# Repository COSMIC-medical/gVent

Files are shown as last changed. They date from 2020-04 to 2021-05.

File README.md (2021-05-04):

# The Gravity Ventilator (gVent)

Video introduction to the design [here](https://www.youtube.com/watch?v=yVxmjUQLIBw)
### A COSMIC Medical Project

This repository contains all the design files necessary to assemble a gravity ventilator. Please read license.pdf before using any of the files to understand the liabilities and limitations you are responsible for by using this repository.

NOTE: At this point, this is not a medical device, meaning that the device is NOT medically approved for human use, and as such, improper use can result in harm or death of anyone using the ventilator. It is still in its development stages and any use in a clinical setting should be under the strict consultation and supervision of qualified healthcare experts and/or qualified biomedical engineers.

## Background on the Idea

In February 2020 amidst the CoVid-19 pandemic, concerns about a global shortage of ventilators began to surface and these discussions rapidly became a reality. We sought out to find a local solution to the rapidly evolving crisis, working alongside the [hundreds of open-source projects worldwide](https://github.com/PubInv/covid19-vent-list), aimed at tackling the same problem.

We believe that we add a novel solution to a landscape dominated by automated bag-valve mask compression devices. Built using readily-available materials and utilizing resources routinely found at a patient’s bedside, our aims were to produce a device capable of being produced at a sub-$100 price point for low-resource settings, as well as a more robust model, both founded using the same principles.
## The Design

Modern commercial ventilators are complex machines with specialized components. According to the Department of Health and Social Care guidance statement on [Rapidly Manufactured Ventilator System Specification (20/03/2020)](), ventilators must meet certain criteria to be considered “clinically acceptable”.

RMVS-compatible ventilators must be capable of providing one of two modes of ventilation. The first is mandatory ventilation, wherein the patient is completely sedated, and all work of breathing must be done by the ventilator, according to preset criteria (e.g. tidal volume, respiratory rate, E/I ratio). Supportive ventilation, on the other hand, is used when the patient can do some work on their own. The machine must be able to sense when the patient is attempting to inhale (and provide inspiratory support), and when the patient is exhaling (and provide expiratory support).

#### __How does it work?__

The basis of the gVent system is gravity, water, and two cylindrical vessels fitted together to create a pressurized system. This pressure can then be used to ventilate a sick patient. The two vessels are each sealed at one end. The larger vessel is filled with water; the smaller vessel is placed inside the larger vessel.

Air is then introduced into the system from the hospital's O<sub>2</sub> outlet. A clinician can thus control the FiO<sub>2</sub> by titrating the amount of hospital air to the amount of delivered O<sub>2</sub>. As this pressurized gas builds up in the system, the top cylinder is displaced upwards from its resting position, commensurate to the weight of the top cylinder (which can have weight added to adjust the pressure).

To deliver air, a valve is opened, releasing the pressurized air/O<sub>2</sub> mixture through to the intubated patient. And with the valve controlled on an electronic circuit, the operator has the ability to control important respiratory parameters, including respiratory rate, I:E ratio, and the volume of air delivered to the patient.

## Bill of Materials

## Installation Instructions

1. The Assembly Instructions document for the gVent can be found at [The COSMIC Medical Website](https://cosmicmedical.ca/gvent-722-warnings-disclaimers).
2. In order to view the code and upload it to the Arduino, download and install the [Arduino IDE](https://www.arduino.cc/en/Main/Software).

## Contributing
See the [CONTRIBUTOR.md](./CONTIBUTOR.md) file in the root of the repository for guidelines and additional instructions.

## Licensing Notes
As per our understanding, hardware is not covered by copyright. However, we present our work under the TAPR OHL license insofar as it applies. All software and documentation is licensed under Apache 2.0.

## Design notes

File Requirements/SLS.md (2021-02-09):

# Gravity Ventilator (gVent) – System Level Specification

***

| Document ID | CSL0133 |
| :-- | :-- |
| Status | DRAFT | 
| Prepared For | COSMIC |
| Project Name | gVent |
| Publish Date | 2020-09-28 |
| Version | 0.8 |

***

# Table of Contents
ii. Document History
1.	[Introduction](#introduction)	
- 1.1	Purpose and scope
- 1.2	Document Structure
- 1.3	Referenced Documents	
2.	System Identification	
- 2.1	System Overview	
- 2.2	Regulatory Environment	
3.	[General](#General)
4.	[Ventilation](#Ventilation)
5.	[Performance](#Performance)
6.	[Alarm](#Alarm)
7.	Major Failure Response
8.	[Reliability](#Reliability)	
9.	[Glossary](#Glossary)

# Document History
| Version | Date | Revision Summary |
| :-- | :-- | :-- |
| 0.1 | 2020-09-24 | First draft |
| 0.2 | 2020-09-25 | Addition of Background information |
| 0.3 | 2020-09-25 | Reformat according to CSL process |
| 0.4 | 2020-09-28 | Addressed internal comments |
| 0.5 | 2020-09-28 | Update requirements numbering to remove duplicates |
| 0.6 | 2020-10-16 | Reformat to GitHub Markdown |
| 0.7 | 2020-10-21 | Update Alarm section| 

# Introduction
This document is a system level specification of the gravity Ventilator (gVent) at a level of abstraction appropriate for clinicians, including respiratory therapists, anesthesiologists, and intensivists. gVent is a low-cost ventilator which provides a constant inspiratory pressure, hence reducing the risk of barotrauma which is inherent in many low-costs ventilator designs. 
### Purpose and scope
This document identifies all the functionalities provided by the gVent. This specification is a placeholder for the system’s requirements described at an appropriate level of abstraction that allows them to be understood by clinicians. The purpose of these functional systems requirements is to make sure that all stakeholders have a common understanding of the entire scope.  
These requirements are expressed at the system level, i.e., the function of the system that will be implemented by the combination of software, hardware, sensors, actuators, other electronics, mechanical and electrical components. Each requirement is a “shall statement”, i.e., a sentence that uses the modal verb “shall” to mark these sentences as a “formal requirement”.  These shall statements are accompanied by additional sentences (inter-woven with the shall statements) and graphics that clarify these shall statements. 
At this level of abstraction, the requirements can sometimes be intentional, e.g., it is acceptable to use a phrase such as “The system shall provide the user a means of adjusting the desired pressure …” without explicitly describing the details such as whether such adjustments are made using a knob or some other method. Although the level of abstraction for these requirements is “high”, this specification also incorporates whatever is currently known about the need to handle abnormal conditions through alarms or other means, e.g., transition to a safe state.

### Document Structure
Section 2 of this document gives an overview of the system, its business motivations and its regulatory environment. The next sections provide system requirements according to their scope, e.g., functional, performance.

### Referenced Documents
The following documents are referenced in this specification:
[1] UK Medicines & Healthcare products Regulatory Agency, Specification for Rapidly Manufactured Ventilator System (RMVS), 28 April 2020 [RMVS](https://assets.publishing.service.gov.uk/government/uploads/system/uploads/attachment_data/file/879382/RMVS001_v4.pdf)
[2] A brief for engineers, by a doctor, on hacking a ventilator for surge capacity in Covid19 patients. Vol 1: Ventilator Design Brief. Dr Erich Schulz, MBBS, FANZCA, Brisbane, Australia. [Brief_vol1](https://docs.google.com/document/d/1sdrKYQ0mDOu4bJum6Fx6piRutIJovo7UqFKYHHxUD5A/edit#heading=h.zfqx8qqil1g1)
[3] Brief, Vol 2: Hardware. Dr Erich Schulz, MBBS, FANZCA, Brisbane, Australia. [Brief_vol2](https://docs.google.com/document/d/1SBT8auegsJCKCVMBHFLWaVo8rKbs0zsJc3dDVAqeADE/edit#heading=h.sx9qnelsso49)
[4] Brief, Vol 3: Software. Dr Erich Schulz, MBBS, FANZCA, Brisbane, Australia. [Brief_vol3](https://docs.google.com/document/d/1-eV7ClGCTgaqPug7u9ovE_s-U6J5s8Hzc3XAalkEgVE/edit#heading=h.sx9qnelsso49)

# System Identification
## System Overview
The gravity Ventilator (gVent) intends to provide mechanical ventilation to patients. The gravity Ventilator aims to deliver controlled pressure ventilation to patients, which appears to be the most useful ventilatory mode with COVID ARDS patients, as high pressures can easily lead to barotrauma.

At minimum, the gVent is specified to operate for a few hours to a full day for patients in extremis as per rapidly manufactured ventilator system (RMVS, gov.uk Medicines and Healthcare Products Regulatory Agency)[1] specifications.  gVent will only rely on access to power and wall ports providing a supply of oxygen and filtered air.

## Regulatory Environment

# General 
#### SLS-0001 
gVent **shall** provide ventilation mechanisms to a patient through a system composed of an inspiratory limb and an expiratory limb. 

#### SLS-0005 
gVent **shall** be designed so that the expiratory block can be cleaned and sterilized.

#### SLS-0010
gVent **shall** accept power from 120V sources and 220V sources.

#### SLS-0015
In a power outage situation, gVent **shall**: turn on a visual and sound alarm, and transition seamlessly to external battery power. The external battery shall supply power for a minimum of 20 minutes.

# Ventilation
This section’s requirements focus primarily on providing ventilation. 
#### SLS-0020
gVent **shall** allow the clinician to set the FiO2 between [21%, 100%] in 10% increments. 
gVent relies on the supply of oxygen and filtered air commonly available through wall ports in a clinical environment. 
#### SLS-0025
gVent **shall** achieve ventilation using the filtered air source flow inputs in the range of [0, 40] liters per minutes (L/min) Other than valves, gVent does not intend to use mechanical parts to deliver the Pressure Controlled air flow.

*Note: this is about design, but it is also what makes gVent different from other ventilators. It might be beneficial to include such a requirement.*

Operator adjustable settings include ventilation control parameters such as Respiratory Rate as well as alarm thresholds.

#### SLS-0030
gVent **shall** provide a visual indication of operator adjustable settings and their corresponding values to the Clinician through an LCD display.

#### SLS-0035
gVent **shall** provide an interface for the clinician to modify operator adjustable settings.

#### SLS-0040
gVent **shall** provide a clinician interface to start and stop the ventilation.

*Note: a requirement may be needed to discuss emergency stop if it is different from normal stop.*
Mechanical ventilation is generally performed in either a Pressure Control mode or a Volume control mode while many other advanced modes also exist. The Gravity Ventilator will deliver constant pressure ventilation to patients to avoid the risk of high pressures which can lead to barotrauma.

#### SLS-0045
gVent **shall** deliver air flow to patient in Pressure Controlled mode for an inspiratory pressure range [10,40] centimeters of water (cm H2O).

*Note: Pressure Controlled mode includes two sub-modes of operations: the ‘timed’ and ‘triggered’ modes.*
Mechanical ventilation is generally performed in either a Pressure Control mode or a Volume control mode while many other advanced modes also exist. The Gravity Ventilator will deliver constant pressure ventilation to patients to avoid the risk of high pressures which can lead to barotrauma.
#### SLS-0045
gVent **shall** deliver air flow to patient in Pressure Controlled mode for an inspiratory pressure range [10,40] centimeters of water (cm H2O).

*Note: Pressure Controlled mode includes two sub-modes of operations: the ‘timed’ and ‘triggered’ modes.*

#### SLS-0050
gVent **shall** allow the clinician to select either the ‘timed’ or ‘triggered’ Pressure Controlled modes of operations

#### SLS-0055
In the ‘Timed’ mode of operation, gVent **shall** deliver pressure-controlled air flow based on the Respiratory Rate, the Inspiratory:Expiratory Ratio and the Inspiratory Pressure set by the clinician.

This is the situation where the patient is fully unconscious.

#### SLS-0060
In the ‘triggered’ mode of operation, gVent **shall** detect patient breath initiation and deliver pressure-controlled air flow for a set duration.
If gVent does not detect a breathing action within the period specified by the Respiratory Rate, gVent **shall** force the breathing actions.

This is the situation where the patient is semi-conscious. 

Positive End Expiratory Pressure maintains the patient's airway pressure above the atmospheric level by exerting pressure that opposes passive emptying of the lung. 
This is important for some patient lung medical conditions. 
This pressure is typically achieved by maintaining a positive pressure flow at the end of exhalation. This pressure is measured in centimeters of water, cmH2O.

#### SLS-0065
gVent ventilation modes **shall** achieve a defined Positive End Expiratory Pressure (PEEP) range between [0, 30] centimeters of water (cm H2O).

#### SLS-0070
gVent **shall** accommodate a Respiratory Rate between [1,60] breath per minute (bpm).

#### SLS-0075
gVent **shall** accommodate an Inspiratory:Expiratory ratio from 1:1 to 1:5.

Inspiratory:Expiratory ratio refers to the ratio of inspiratory time:expiratory time. In normal spontaneous breathing, the expiratory time is about twice as long as the inspiratory time

#### SLS-0140
gVent **shall** allow the clinician to change adjustable settings during ventilation.

While the clinician can change the adjustable settings during ventilation. This includes changing the mode of operation of the ventilator (time vs Trigerred).

# Performance
#### SLS-008
When a parameter exceeds a set alarm threshold, gVent **shall** trigger the alarm within 1/10 second.

#### SLS-0085
gVent **shall** provide real-time monitoring of parameters related to alarms. Each parameter shall be monitored every 1/10 second.

#### SLS-0090
gVent **shall** detect a Start action initiated by the clinician within 1/10 second and start the actual ventilation process within 5/10 second.

#### SLS-0095
gVent **shall** detect a Stop action initiated by the clinician within 1/10 second.

#### SLS-0100
In the ‘Triggered’ mode of operation gVent **shall** detect changing breath cycle every 2/10 second and adjust ventilation according to the sensed Respiratory Rate.

# Alarm
During the ventilation procedure gVent shall sound audible alarms when thresholds are exceeded for a given amount of time for a pre-defined set of alarm parameters. These parameters are described in a [notion](https://www.notion.so/Alarm-Documents-790364c4ae0842dabbaa4d9f6f67821b#a75de7f03972482d9c61786357f3d80f).

#### SLS-0120
gVent **shall** monitor a set of alarm conditions and generate alarms  based on corresponding alarm parameters:
- Inspiratory pressure: high and Low
- Positive End Expiratory Pressure (PEEP): high and low
- Tidal volume: high and low
- percentage of CO2 at expiration: high and low 
- Oxygen supply failure
- Airway occluded
- Patient disconnect
- Circuit Leak
- Power Failure
- Battery Failure
- Low Battery
- Pressure Sensor failure
- Flow sensor failure

#### SLS-0125
when an alarm condition is present for a predefined alarm time for this condition, gVent **shall** turn on a visual and auditory alarm and display the alarm level until the alarm condition is not present anymore. 

The alarm levels are info/notice, alert, warning, alarm, and critical. Each alarm condition is affected to a unique alarm level.

#### SLS-0130
gVent **shall** allow the clinician to mute a non-critical alarm for 60 seconds.

# Major Failure Response
This section addresses gVent response to abnormal situation that go beyond alarms and involve actuation. 

The safe state of gVent is an open circuit that supplies a high flow of oxygen. 

#### SLS-0135
In the event of a major failure gVent **shall** revert to the safe state.

# Reliability
#### SLS-0105
gVent **shall** run with no interruption and no performance degradation for a duration of at least 14 days.

*** 

## Glossary
| Term |  Abbreviation | Definition |
| :--- | :-- | :--- |
| Pressure Controlled Ventilation | PCV | A set pressure is delivered for the period of inspiration and the volume achieved is measured and displayed. Ideally PRVC, an adaptive mode where the tidal volume is set, and the lowest possible pressure is delivered to achieve this volume. PCV where the user has to provide the adaptive control to achieve tidal volume is only acceptable if the tidal volume delivered is clearly displayed and the user can set patient specific upper and lower tidal volume alarms to alert to the need to adjust the pressure [1].
| Volume Controlled Ventilation | VCV | The user sets a tidal volume and Respiratory Rate. The tidal volume is delivered during the inspiratory period. Acceptable only if additional pressure limiting controls are available, see Inspiratory Pressure section [1].
| Positive End Expiratory Pressure | PEEP | The pressure maintained in the breathing system during expiration[1].
| Respiratory Rate | RR | The number of breathing cycles every minute[1].
| Inspiratory: Expiratory ratio | I:E | The proportion of each breathing cycle that is spent breathing in compared to breathing out.
| FiO2 | |  inspired oxygen proportion.[1]
| Critical Systems Labs | CSL | Critical Systems Labs is a Canadian-owned engineering consultancy with expertise in the management of safety risk and security vulnerabilities associated with complex hardware/software intensive systems. CSL has partnered with COSMIC Medical to assist in the project development, software process, and risk analysis of the gVent design-build. 
| Centimeters of water | cmH2O | Unit of pressure used in clinical settings for ventilation systems.

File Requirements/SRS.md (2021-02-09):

# gVent - Software Requirement Specification

## Introduction

This Software Requirements Specification (SRS) specifies the required
functionality of the gVent software. It is a refinement and elaboration
of that portion of the system level behaviour allocated to software.
The required software functionality is specified in terms of interactions
with the gVent Platform, which is an abstract view of the software/hardware
interface. The contents of this SRS are independent of board specific
details, i.e., porting gVent to a different target board should not
necessitate changes to this SRS.  In addition to “shall statements”,
this SRS includes a dictionary which also provides essential information
about the required functionality.  The requirements specified in this SRS
are used directly by software developers to develop the gVent source code.  
These requirements are also used directly for requirements-based testing
of the software. Every aspect of the system level behaviour, as specified
in the System Level Specification (SLS) should be traceable to one or
more requirements in this SRS unless the SLS requirement is entirely
unrelated to the software functionality.  Every requirement in this
SRS should be traceable to at least one SLS requirement unless the SRS
requirement is concerned with an internal software mechanism that
facilitates the implementation of other SRS requirements.

## Purpose

Present the software requirements in a not so low level of abstraction
for software developers to start implementation. These requirements are
 used to drive requirements-based testing of the gVENT software.

The first draft of this document will only contain a partially worked
example of how a single system level requirement at the SLS level
can be refined and elaborated into software requirements specified in
the SRS, and then into source code for the gVent Platform. The requirements
shown below are draft requirements only.  In this example, the specification
of a single system requirement, SLS-0070, is shown below.  This is followed
by a set of software requirements, SRS-XXXX.  

## Scope

The requirements described in this document descend directly from the SLS.
Only software requirements. Some other requirements for the non software element
of the system would be written elsewhere. The requirements for the platform
where the software will run will be documented in a Platform Specification (PS)
link here and in a Hardware Abstraction Specification(HAS) link here. The
requirements in this specification should be expressed at a level of abstraction
“just above” the platform implemented by an RTOS or cyclic executive on top
of bare hardware, i.e., these requirements use a purely functional (“blackbox”)
view of the platform as a basis for specifying requirements at this level.

## Background

### GVent

The gravity Ventilator (gVent) intends to provide mechanical ventilation
to patients. The gravity Ventilator aims to deliver constant pressure
ventilation to patients, which appears to be the most useful ventilatory
mode with COVID ARDS patients, as high pressures can easily lead to barotrauma.

### SRS

While the SLS level of specification is expressed at a level of abstraction
suitable for a clinician.  The SRS level of specification is a “black box”
view of the software functionality. In the SRS, references to inputs and
outputs are clearly identified, but referenced only in terms of an abstract
view of the software/hardware interface. These shall statements are
accompanied by additional sentences (inter-woven with the shall statements)
and graphics that clarify these shall statements.

All project-specific terminology (words and phrases) are defined in the 
glossary,including, but not limited to inputs/outputs, state variables and
system parameters.

### Notation

Each software requirement present in the SRS is clearly identified by a
unique identifier or the form SRS-XXXX where XXXX is unique within the
set of requirements defined in the SRS. A requirement in the SRS is a
“shall statement”, i.e., a sentence that uses the modal verb “shall” to
mark these sentences as a “formal requirement”.  

 In general, every functional requirement is an instance of one of the 
 following:

- A requirement that specifies an “effect” in response to a stimulus.
- A requirement that defines a condition.

Additionally, the requirements in this document follow the following rules:

- Use one shall for each requirement.
- Write concise and complete requirements. A requirement should fully define
a functionality.
- Write testable requirements. Avoid negative requirements, since they are
difficult to verify. Use the active voice.
- Write requirements at an appropriate and consistent level of granularity.
- Build robustness into the requirements by thinking through how the software
will respond to abnormal inputs.
- Include rationale and background for requirements to clear the requirement
meaning or how it is related to a SLS.
- Avoid ambiguous requirements. Avoid using and/or or using the slash (/)
symbol to separate two words. Use adverbs ending in -ly cautiously (e.g.,
reasonably, quickly, significantly, and occasionally). Use pronouns cautiously
 (e.g., it or they). It is typically better to repeat the noun. Avoid words
 that sound alike or similar.
- Minimize or avoid the use of words that indicate multiple requirements,
such as unless or except.

### Document Structure

[Section 2](#system-description) of this document describes the software with
its inputs and outputs.
The rest of the document contains the software requirements, while in
[Section 4](#dictionary) the terms used in this document are defined.

## System Description

### System inputs
The inputs of the system are either the measured values or values entered by
a clinician in the system.

| Name            | Data type | Units | Validity Criteria   | Failsafe Value |
| ------------------------- | --------- | ----- | ------------------- |------|
| selected respiratory rate | int       | bpm   | [4, 50]             | 15   |
| selected I:E ratio        | int       |       | [1, 5]              | 1    |
| measured inspiratory pressure | int   |       | [-5, 40]            |      |
| measured inspiratory flow | int       | cmH2O | [-250, 250]         |      |
| measured expiratory pressure | int    | SPLM  | [-5, 40]            |      |
| measured expiratory flow  | int       | cmH2O | [-250, 250]         |      |
| selected input for modification | enum| NA    | {RR, TV, I:E ratio} | None |
| Acceptable low PEEP value | int       | cmH2O | [0, 30]             | 4    |
| Acceptable breath per minute | int    | bpm   | [10, 100]           | 30   |
| Acceptable exhaled tidal volume | int | mL    | [150, 600]          | 300  |
| Ventilation mode          | enum      | NA    | {triggered, timed}  | timed|

### Defined values
*Defined values* are values that are calculated or obtained in some non-trivial
manner.

| Name          | Data type | Units | Validity Criteria | Failsafe Value | Computation|
| ---------------------- | --- | ---- | --------- | -- | ----------- |
| breath cycle duration  | int | ms   |           |    | 60 000 / RR |
| circuit pressure       | int | cmH2O| [10, 40]  |    | mean(measured inspiratory pressure, measured expiratory pressure)|
| measured tidal volume  | int | mL   | [20, 1500]|    |             |

### System outputs

| Name            | Data type | Units | Validity Criteria   | Failsafe Value |
| ------------------------- | --------- | ----- | ----------- |-------|
| Power led (green led)     | enum| NA  | {on, off}           | off   |
| Power led (yellow led)    | enum| NA  | {on, off}           | off   |
| Alarm led (red led)       | enum| NA  | {on, off}           | on    |
| inspiratory valve         | enum| NA  | {open, close}       | open  |
| expiratory valve          | enum| NA  | {open, close}       | open  |
| tank valve                | enum| NA  | {open, close}       | close |
| buzzer                    | enum| NA  | {on, off}           | on    |

since the following are also displayed to the clinician. They should be part of
this table.
- measured exhaled Tidal volume (expired).
- selected I:E ratio.
- selected RR.
- computed Inspiration times.
- computed expiration times.
- minute volume.
- measured PIP.
- mean inspiratory pressure (average over one inspiration).
- selected ventilation mode.
- measured leak percentage. 

## Requirements

### SRS-0000:  Start ventilation
Upon system power-on, gVent **shall** default to timed-mode pressure-control ventilation (PCV).
This requirement might not reflect the final behaviour of the system. 

### SRS-0001:  computation of breath cycle duration
Related to: [SLS-0055.](SLS.md#SLS-0055)
The {duration of a breath cycle} **shall** be determined between breaths (i.e., just before starting a new inspiration) according to the \<selected respiratory rate>.  
This means that gVent will compute the length of the next breath cycle before starting this breath cycle.
The {duration of a breath cycle} is given in ms.  
The computation is as follows:  60 000 / <selected respiratory rate>. The {duration of a breath cycle} is in ms. The division is an integer division. Utilisation of an integer division is acceptable in this case since the RR is given in breath per minute the  error introduced by this division is not significant. 
The {duration of a breath cycle} is an input to the ventilation SRS requirements SRS-0010 and SRS-0025.

### SRS-0002:  computation of circuit pressure
The {circuit pressure} **shall** be determined as the mean of the \<measured inspiratory pressure> and the \<measured expiratory pressure>. The computation is as follows: (\<measured inspiratory pressure> + \<measured expiratory pressure>) / 2. The division is an integer division. This is acceptable since a +/- cmH20 error in the circuit pressure is acceptable.  
The {circuit pressure} is an input to the ventilation SRS requirements SRS-0010, SRS-0015, SRS-0020, and SRS-0025.  
  
### SRS-0003:  impossible computation of circuit pressure
Related to [SRS-0002.](SRS.md#SRS-0002)
If either of the  \<measured inspiratory pressure> or the  \<measured expiratory pressure> necessary to compute the circuit pressure is not available, gVent **shall** transition to DSS in less than TIME_TO_TRANSITION_TO_DSS_CSP ms.   
A measured input such as the  \<measured inspiratory pressure> or the  \<measured expiratory pressure>  is not available when the platform returns the unavailable value. This could be caused by the sensor not sending any values or the value sensed being outside of the valid bounds. 

### SRS-0004 : RR default failsafe value
If the \<selected respiratory rate> is not available the RR **shall** be set equal to the default failsafe value (see table for value).  
The value for respiratory rate selected by the clinician is not available when the platform returns the unavailable value. This could be caused by the clinician never setting this value or setting this value outside the validity bound for this value, or any other error in the hardware leading the platform to read a value out of the validity bounds.

### SRS-0010: PC timed mode start inspiration
Related to: [SLS-0055.](SLS.md#SLS-0055)
While in ‘timed mode’, at the start of the current breath cycle, if the {circuit pressure} *is less than or equal to* MAX_CIRCUIT_PRESSURE_FOR_OPENING_INS_VALVE_CSP cmH2O gVENT **shall** command the inspiratory valve to open. 

### SRS-0011: PC timed mode start inspiration pressure to high
Related to [SRS-0010](SLS.md#SLS-0010), [SLS-0055.](SLS.md#SLS-0055)
While in ‘timed mode’, at the start of the current breath cycle, the {circuit pressure} is greater than MAX_CIRCUIT_PRESSURE_FOR_OPENING_INS_VALVE_CSP cmH2O, gVent **shall** transition to DSS in less than TIME_TO_TRANSITION_TO_DSS_CSP ms. 

### SRS-0012: PC timed mode start inspiration closes expiratory valve
Related to: [SLS-0055.](SLS.md#SLS-0055)
While in ‘timed mode’, at the start of the current breath cycle, if the {circuit pressure} is less than or equal to MAX_CIRCUIT_PRESSURE_FOR_OPENING_INS_VALVE_CSP cmH2O gVENT **shall** command the expiratory valve to close. 

### SRS-0013: PC timed mode start inspiration closes tank valve
Related to: [SLS-0055.](SLS.md#SLS-0055)
While in ‘timed mode’, at the start of the current breath cycle, if the {circuit pressure} is less than or equal to MAX_CIRCUIT_PRESSURE_FOR_OPENING_INS_VALVE_CSP cmH2O gVENT **shall** command the tank valve to close. 

### SRS-0015: PC timed mode end inspiration
Related to [SRS-0010](SLS.md#SLS-0010), [SLS-0055.](SLS.md#SLS-0055)
While in ‘timed mode’, at the start of the current breath cycle, the {circuit pressure} is greater than MAX_CIRCUIT_PRESSURE_FOR_OPENING_INS_VALVE_CSP cmH2O, gVent **shall** transition to DSS in less than TIME_TO_TRANSITION_TO_DSS_CSP ms. 

### SRS-0020: PC timed mode start expiration
Related to: [SLS-0055.](SLS.md#SLS-0055)
While in ‘timed’ mode,  \<selected inspiration time> ms after the start of  the current breath cycle, if the {circuit pressure} is less than MIN_CIRCUIT_PRESSMIN_CIRCUIT_PRESSURE_FOR_OPENING_EXP_VALVE_CSPURE_FOR_OPENING_EXP_VALVE_CSP cmH2O,  gVENT **shall** command the expiratory valve to open and tank valve to open.  
Note: VALVE_CLOSING_TIME_CSP is used to ensure under normal conditions that the inspiratory valve is closed before the expiratory valve opens.

### SRS-0021: PC timed mode start expiration
Related to: [SLS-0055.](SLS.md#SLS-0055)
While in ‘timed mode’, VALVE_CLOSING_TIME_CSP milliseconds after the end of the inspiratory for the current breath cycle,  if the {circuit pressure} is greater or equal than the MIN_CIRCUIT_PRESSURE_FOR_OPENING_EXP_VALVE_CSP cmH2O, gVent **shall** transition to DSS.

### SRS-0025: PC timed mode end expiration
Related to: [SLS-0055.](SLS.md#SLS-0055)
While in ‘timed’ mode, VALVE_CLOSING_TIME_CSP milliseconds (<1000) before the end current breath cycle, gVENT **shall** command the expiratory valve to close and tank valve to close.

## DSS

### SRS-0050 DSS definition
In DSS all the valves shall  be open.

### SRS-0051 DSS led
In DSS gVent shall turn on the alarm led.

### SRS-0052 DSS sound alarm
In DSS gVent shall turn off the alarm buzzer.

### SRS-0053 DSS display
In DSS gVent shall display “DSS”.

### SRS-0054 DSS persistence
Once gVent has transitioned to the DSS, it shall remain in the DSS indefinitely, until it is power-cycled.

## Alarm Requirements
Reference: https://www.notion.so/Alarm-Documents-790364c4ae0842dabbaa4d9f6f67821b#a75de7f03972482d9c61786357f3d80f use this as the basis of alarms

### ALA5 
#### SRS-0104: computation of {running breath count}
Related to: ???
Every ALA5B_FREQUENCY_CSP ms, the {running breath count} shall be computed as the running average of the number of times the inspiratory valve changes from open to closed in BREATH_COUNT_TIME_CSP ms.
ALA5B_FREQUENCY_CSP = 1 second
BREATH_COUNT_TIME_CSP  = 30 seconds

#### SRS-0105: High RR Alarm LED (ALA5B)
Related to: ???
gVent shall turn on the alarm led if {running breath count} is greater than <acceptable breaths per minute averaged over 30 sec>.

#### SRS-0106: High RR Alarm Buzzer On (ALA5B)
Related to: ???
gVent shall turn on the alarm buzzer if {running breath count} is greater than <acceptable breaths per minute averaged over 30 sec>.

#### SRS-0107: High RR Alarm Buzzer Off (ALA5B)
Related to: ???
gVent shall turn off the alarm buzzer if {running breath count} is lower than <acceptable breaths per minute averaged over 30 sec>.

#### SRS-0108: High RR Alarm display (ALA5B)
Related to: ???
gVent shall write the alarm level (i.e., ???) on the LCD if {running breath count} is greater than <acceptable breaths per minute averaged over 30 sec>.
The breaths per minute is calculated then averaged over 30 seconds, the calculated value is compared to the value specified by the cilician on the device. If the calculated value is greater than the set value then the high RR alarm will be triggered.

### ALA9

#### SRS-0110: Low Tidal Volume Alarm (ALA9)
Related to: ???
gVent Shall turn on Low Tidal Volume Alarm if <measured exhaled tidal volume> is less than the <acceptable exhaled tidal volume value>.
If the exhaled tidal volume is measured below the tidal volume value specified by the clinician on gVent then the Low Tidal Volume Alarm will be triggered.

### ALA7

#### SRS-0120: Low PEEP Alarm (ALA7B)
Related to: ???
gVent Shall turn on Low PEEP Alarm if <measured pressure at the expiratory end> is below <acceptable/set low PEEP value> and is sustained for more then MAX_TIME_BELOW_PEEP_CSP.
If the positive end-expiratory pressure (PEEP) is measured below the specified value, for more than a specified time period, trigger the Low PEEP Alarm to indicate the presence of a leak or disconnect in the system. For a period less than the specified time do not trigger the Low PEEP Alarm as it is an acceptable low PEEP event for assisted breathing, or a cough.

### ALA ??? 

#### SRS-0130: High Airway Pressure Alarm ()
Related to: ???
gVent Shall enable the buzzer and LED, including showing values on screen, of High Airway Pressure Alarm if <measured pressure at inspiratory end> is gradually increasing instead of decreasing and is sustained for more than <(add time duration of pressure)> at <(add normal inspiratory pressure, need to look if there is a standard for this)>. 
For events where the period is less than <(probably a short time period)>, do not trigger alarm.

## Dictionary

The names of configurable System Parameters are in all-uppercase, e.g., `VALVE_CLOSING_TIME_CSP`.
The names of inputs are enclosed within matching angle brackets, e.g., <selected respiratory rate>.
The names of the defined values are enclosed within braces, e.g., {circuit pressure}.

**Pressure Control** – A form of controlled ventilation, where the clinician sets a specific pressure that the ventilator delivers to the patient. The amount of volume delivered at that set patient varies based on patient factors (eg the ability of the lungs to expand (compliance)).

**Peak Inspiratory Pressure (PIP)** – The highest level of pressure that is applied to the lungs during inhalation.

**Standard Liter Per Minute (SLPM)** - Flow rate unit of measurement.

**\<selected /respiratory rate>** – Minimum number of breaths per minute.

**\<selected /inspiration time>** - The duration of an inspiration as selected by the clinician.

**\<selected I:E ratio>** – the ratio of inspiration/expiration in one breath cycle. 

**\<selected tidal volume>** – The lung volume or the volume of air displaced between inhalation and exhalation.

**\<measured expiratory pressure>** – The measured pressure in cmH2O at the inspiratory valve.

**\<measured inspiratory pressure>** – The measured pressure in cmH2O at the inspiratory valve.

**\<acceptable/set low PEEP value>** - The value for lowest acceptable PEEP value as set by the clinician into the machine. 

**\<acceptable breaths per minute>** - The value for the acceptable number of 
breaths per minute as set by the clinician.  This is an average rate for 
30 seconds.

**\<measured exhaled tidal volume>** - The exhaled tidal volume measured by the system.

**\<measured minute volume>** - The sum of the tidal volume over the last minute. 

**\<acceptable exhaled tidal volume value>** - The acceptable exhaled tidal volume value as inputted and specified by the clinician on the device. 

**{circuit pressure}** – The instantaneous pressure seen by the patient in cmH2O. The degree of precision for this is ???. 

**{number of breaths per minute averaged over 30 seconds}** - The measured Breaths Per Minute of the System averaged over 30 seconds.

`VALVE_CLOSING_TIME_CSP` – the normal amount of time in ms required for either valve to fully close upon command from the fully open position.

`MAX_CIRCUIT_PRESSURE_FOR_OPENING_INS_VALVE_CSP` – The maximum pressure in the circuit in cmH2O so that the inspiratory valve may be opened.
 
`MIN_CIRCUIT_PRESSURE_FOR_OPENING_EXP_VALVE_CSP` – The minimum pressure in the circuit in cmH2O so that the expiratory  valve may be opened.
 
`MAX_PRESSURE_CSP` – The maximum circuit pressure in cmH2O  that can be applied to the patient lungs. 

`MAX_PRESSURE_PERSISTANCE_CSP` – the maximum time in ms for which the pressure can be `MAX_PRESSURE_CSP` without endangering the patient.

`MIN_PRESSURE_CSP` – the minimum circuit pressure in cmH2O that can be applied to the patient lungs.

`MIN_PRESSURE_PERSITANCE_CSP` – the maximum time in ms for which the pressure can be `MIN_PRESSURE_CSP` without endangering the patient.

`MAX_TIME_BELOW_PEEP_CSP` – the maximum time in ms for which the pressure can be below <acceptable/set low PEEP value> before triggering the Low PEEP Alarm (ALA7B).

`BREATH_COUNT_TIME_CSP` - the number of ms that is used to compute the {running breath count}.

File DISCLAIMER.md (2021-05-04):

# Disclaimer of Warranties

You acknowledge that the Content is in research phase and all outcomes from use of the Content are not known. 
YOUR USE OF THE SITE AND THE CONTENT LOCATED ON THIS SITE AND ANY LINKED SITE, INCLUDING THE DESIGN SPECIFICATIONS, IS AT YOUR OWN RISK. 
THE SITE AND ITS CONTENT, INCLUDING THE DESIGN SPECIFICATIONS LOCATED ON THE SITE OR ANY LINKED SITE, ARE PROVIDED ON AN “AS IS” AND “AS AVAILABLE” BASIS.

COSMIC MEDICAL MAKES NO REPRESENTATIONS, WARRANTIES OR COVENANTS, WHETHER STATUTORY, EXPRESS, IMPLIED, BY COURSE OF COMMUNICATION OR DEALING, OR OTHERWISE WITH RESPECT TO THE CONTENT, INCLUDING THE DESIGN SPECIFICATIONS, AND ANY RESULTING DEVICE. COSMIC MEDICAL SPECIFICALLY DISCLAIMS ANY WARRANTY WITH REGARD TO FITNESS FOR ANY PARTICULAR PURPOSE, MERCHANTABILITY OR NON-INFRINGEMENT. 

WITHOUT LIMITING THE GENERALITY OF THE FOREGOING, COSMIC MEDICAL MAKES NO WARRANTY OF ANY KIND THAT THE CONTENT, INCLUDING THE DESIGN SPECIFICATIONS, AND ANY RESULTING DEVICE OR THE RESULTS OF THE USE OF SUCH DEVICE WILL MEET YOUR OR ANY THIRD PARTY’S REQUIREMENTS, OR ACHIEVE ANY INTENDED RESULT OR THAT THE USE OF THE DESIGN SPECIFICATIONS TO MAKE A DEVICE WILL COMPLY WITH INTERNATIONAL, FEDERAL, STATE OR MUNICIPAL LAWS AND REGULATIONS REGARDING MEDICAL DEVICES OR MEDICAL USES. YOU EXPRESSLY ACKNOWLEDGE AND AGREE THAT COSMIC MEDICAL IS NOT RESPONSIBLE FOR ANY HEALTH PROBLEMS, INJURIES OR DEATH THAT MAY RESULT FROM YOUR OR ANY THIRD PARTY’S USE OF ANY DEVICE RESULTING FROM YOUR USE OF THE CONTENT, INCLUDING THE DESIGN SPECIFICATIONS. IT IS UNDERSTOOD THAT COSMIC MEDICAL DOES NOT PROVIDE MEDICAL OR OTHER HEALTH-RELATED ADVICE.

COSMIC MEDICAL DISCLAIMS ANY RESPONSIBILITY FOR OR ASSURANCES REGARDING THE QUALITY, FUNCTIONALITY, OR SAFETY OF ANY DEVICE RESULTING FROM YOUR USE OF THE CONTENT, INCLUDING THE DESIGN SPECIFICATIONS, OR ANY DEFECT, ERRORS OR MALFUNCTION IN CONNECTION THEREWITH. FURTHER, COSMIC MEDICAL DISCLAIMS ANY RESPONSIBILITY FOR OR ASSURANCES REGARDING ANY COMMENTS, FEEDBACK, INFORMATION OR OTHER KNOW-HOW UPLOADED TO THIS SITE OR ANY LINKED SITE BY ANY USER. YOU RELY ON USER COMMENTS, FEEDBACK, INFORMATION AND/OR KNOW-HOW SOLELY AT YOUR OWN RISK.

YOU UNDERSTAND AND ACKNOWLEDGE THAT: YOU ARE A LEARNED INDIVIDUAL THAT HAS HAD THE OPPORTUNITY TO OBTAIN ANY AND ALL INFORMATION RELEVANT TO THE USE OF ANY DEVICE RESULTING FROM YOUR USE OF THE

CONTENT, INCLUDING THE DESIGN SPECIFICATIONS; YOU HAVE NO OBLIGATION TO USE THE CONTENT, THE DESIGN SPECIFICATIONS OR ANY DEVICE RESULTING THEREFROM AND YOU DO SO IN YOUR SOLE DISCRETION; YOU ARE RESPONSIBLE FOR DETERMINING THE DEGREE OF MONITORING OR OVERSIGHT THAT IS APPROPRIATE IN CONNECTION WITH PATIENT CARE AND THE USE OF ANY DEVICE RESULTING FROM YOUR USE OF THE CONTENT, INCLUDING THE DESIGN SPECIFICATIONS; YOU HAVE ACCEPTED ALL RESPONSIBILITY AND COSMIC MEDICAL RETAINS NO RESPONSIBILITY FOR YOUR USE OF ANY RESULTING DEVICE; AND YOU WILL COMPLY WITH ALL LAWS AND GOVERNMENTAL RULES, REGULATIONS AND GUIDELINES, INCLUDING ANY SAFETY PRECAUTIONS, THAT ARE APPLICABLE TO THE DEVICE OR THE USE THEREOF.

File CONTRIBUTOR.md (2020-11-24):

# gVent Contributor Guidelines

The gVent source code is divided into two layers of abstraction: 1) the Application Layer, and 2) the Platform Layer. The Platform Layer abstracts the details of hardware interaction and presents a consistent interface to the Application Layer. Source code in the Application Layer focuses on control of specific actuators or sensors to faciliate ventilation. Source code in the Platform Layer focuses on writing/read the appropriate hardware addresses.

There is also the hardware abstraction layer (HAL). The platform layer interacts directly with the HAL. The application layer should never interact with the HAL. The HAL is a copy of the generated code from the STMCubeMX IDE.

These layers organized in the respository as follows:

```shell
./
    src/                /* .c files go here... */
        main.c          /* the startup code for gVent */
        application/    /* application layer source code */
        platform/       /* platform layer source code */

    include/            /* .h files go here... */
        main.h
        application/    /* definitions/headers for application layer */
        platform/       /* definitions/headers for the platform layer */

    device/             /* stm32f401re device specific files */

    lib/                /* additional libraries go here... */
        stm32/          /* HAL definitions and source code for STM32 targets */
```

## Application Layer Development

TODO

### Running Application Layer Unit Tests

TODO - something about to run GoogleTest.

## Platform Layer Development

TODO

### Building for STM32F4 Microprocessor Target

The Makefile in the root of this repository contains the relevant compilation, linking to produce a binary that can be uploaded ("flashed") onto the the STM32F401RE microprocessor (the "target").

#### Dependencies

Building and flashing the target requires the following dependencies:

* Standard C build packages - `build-essential`
* USB interface package - `libusb-1.0-0-dev`
* GCC for ARM targets - `gcc-arm-none-eabi`
* ST-Link for flashing the target - `stlink-tools` (on Ubuntu 20.x or above), see the [ST-Link GitHub page](https://github.com/stlink-org/stlink) for details.

This procedure has been tested and validated on a Ubuntu 20.04 LTS Virtual Machine running on a Windows 10 host. Other platforms/setups might require special configurations or dependencies.

#### Command Reference

To build an executable (`gvent.bin`), run the following command from within the project root directory:

```
make clean all
```

To upload or flash the STM32 Nucleo-64 board, use the following command from within the project root directory:

```
make flash
```

#### Additional References

* [Basics of building for STM32F4](https://github.com/sdiemert/stm32f4-basic)
* [Compiling STM32F4 blink using make](https://github.com/sdiemert/stm32f4-blink)
* [Compilinig STM32F4 blink with a timer peripheral using make](https://github.com/sdiemert/stm32f4-timer-blink)

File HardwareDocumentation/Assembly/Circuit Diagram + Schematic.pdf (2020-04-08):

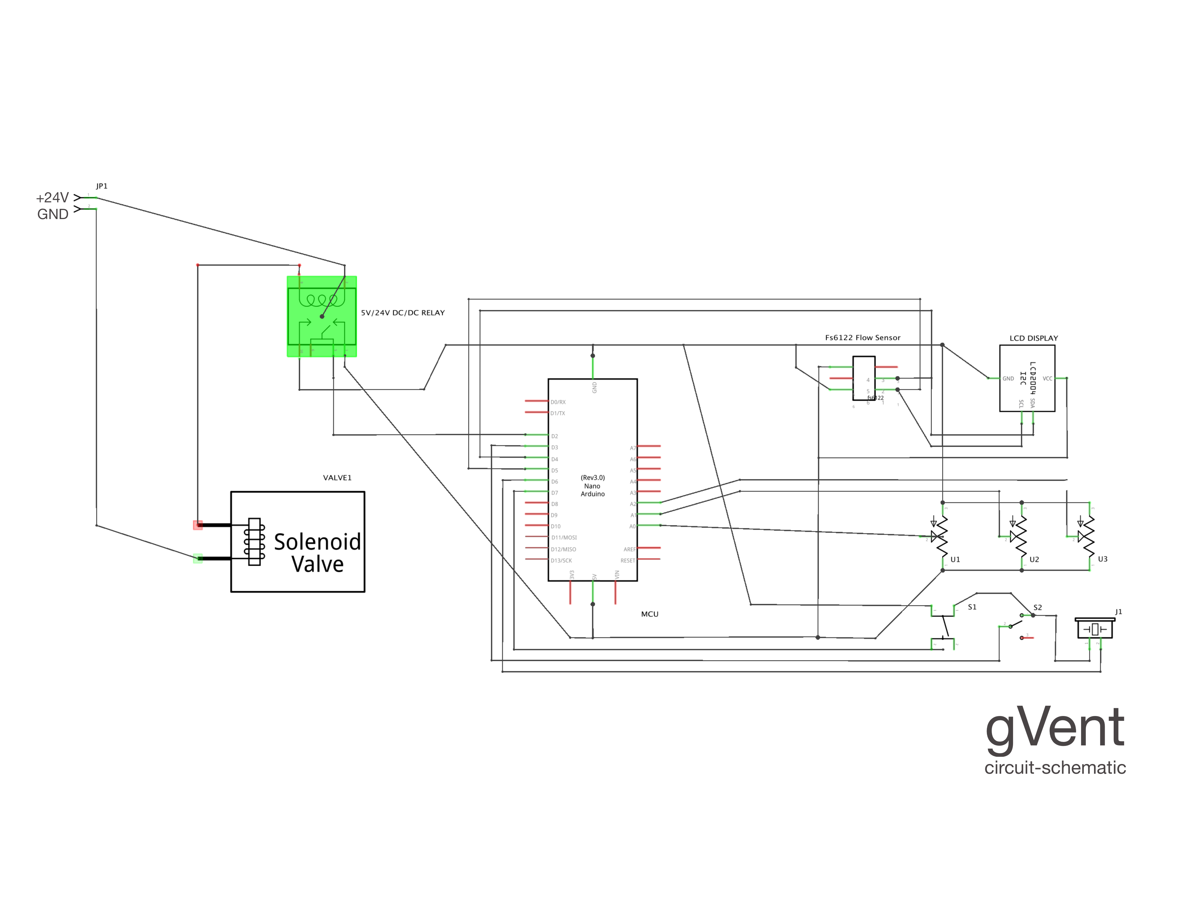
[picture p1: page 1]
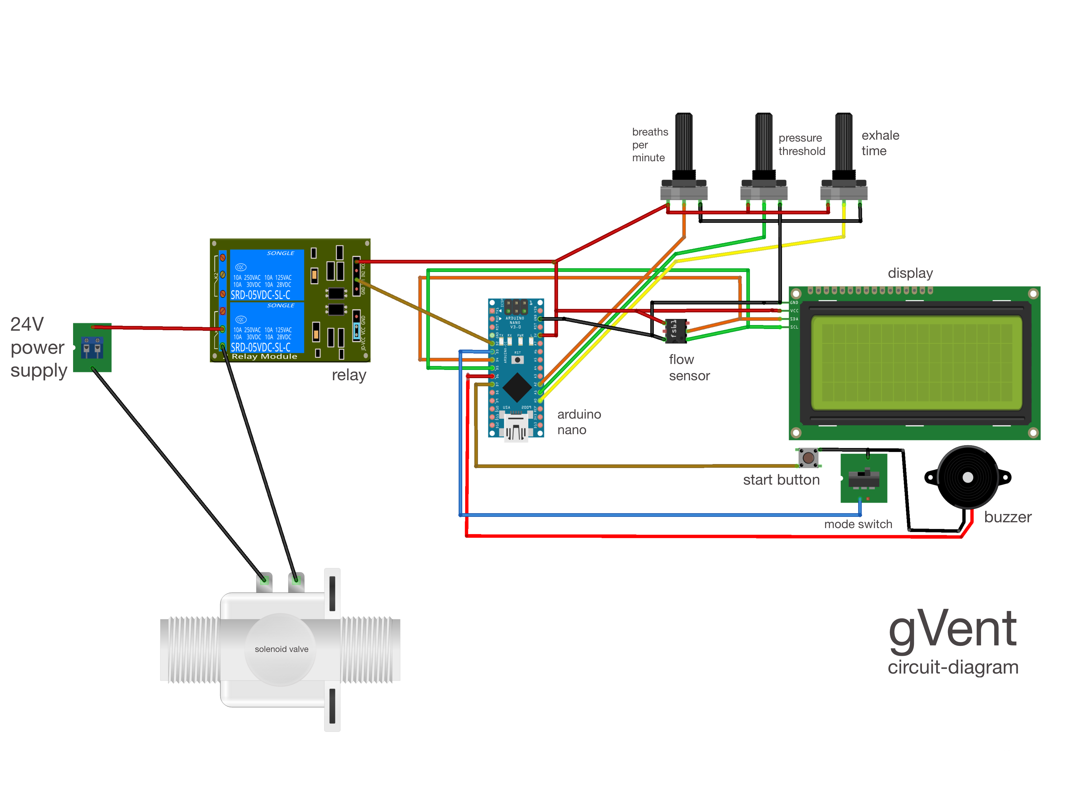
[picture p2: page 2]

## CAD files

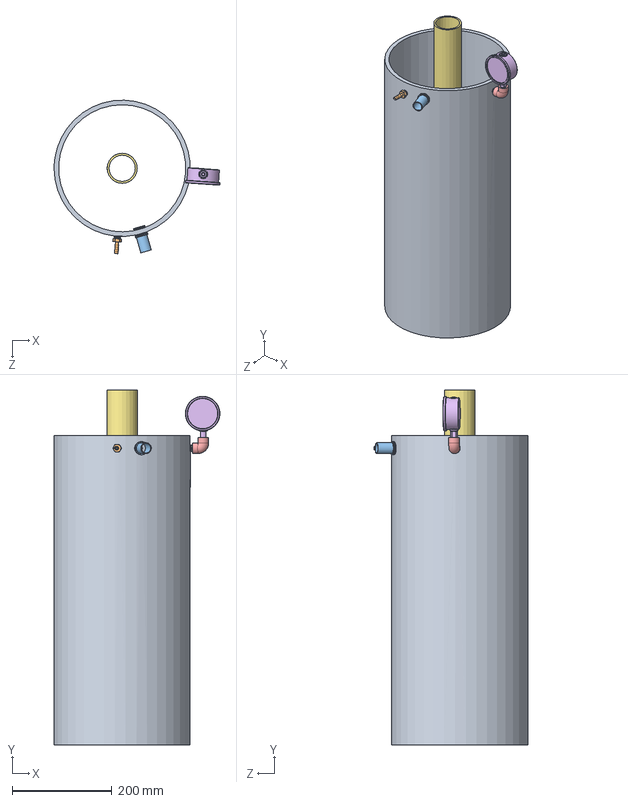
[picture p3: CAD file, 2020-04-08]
HardwareDocumentation/CAD Drawings/SolidWorkds Files/Top Assembly.SLDASM
332.3 x 711.2 x 307.8 mm
PI-002
5372K112_DURABLE NYLON EXTRA-GRIP BARBED TUBE FITTING
9173K740_THK-WALL DK GRAY PVC THRD-ONE-END PIPE NIPPLE
4882K110_THICK-WALL DARK GRAY PVC THREADED PIPE NIPPLE
4596K121_THICK-WALL DARK GRAY PVC PIPE FITTING
3795K133_STAINLESS STEEL GAUGE
PI-003

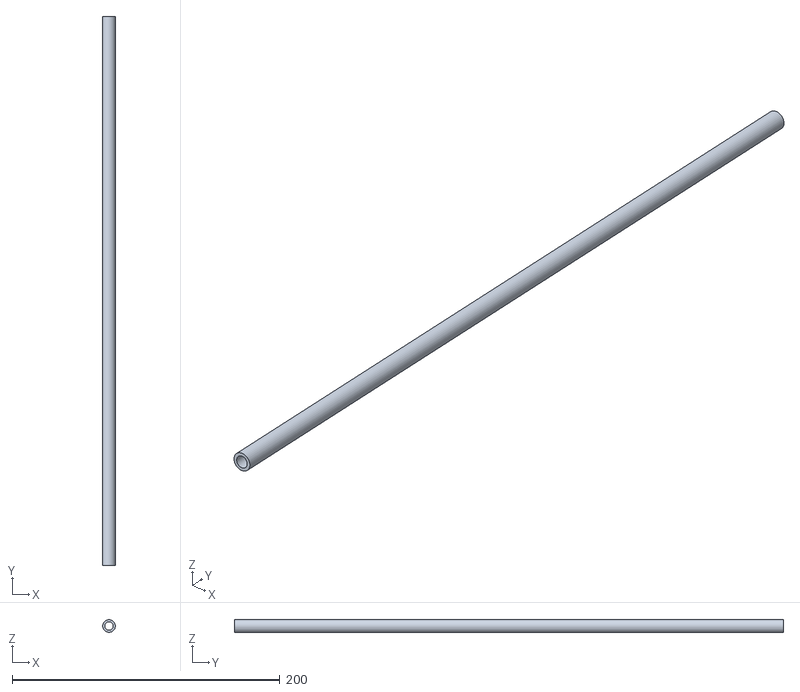
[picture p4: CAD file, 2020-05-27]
HardwareDocumentation/CAD Drawings/STL Files/GA - Bottom assembly-1 5233K520_MASTERKLEER PVC TUBING-1.STL
9.51 x 410.5 x 9.51

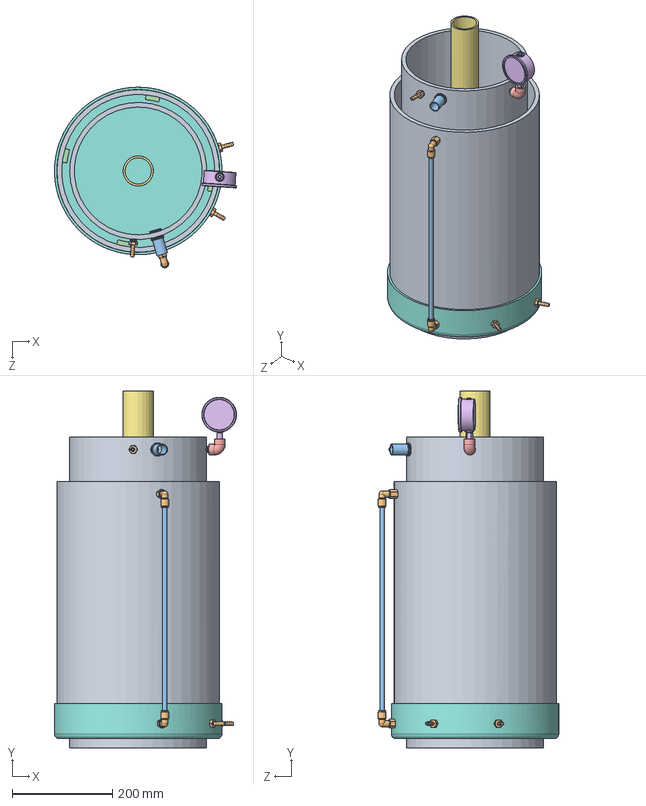
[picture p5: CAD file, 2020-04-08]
HardwareDocumentation/CAD Drawings/SolidWorkds Files/GA1.SLDASM
362.7 x 711.2 x 359.9 mm
PI-002
5372K112_DURABLE NYLON EXTRA-GRIP BARBED TUBE FITTING x 3
9173K740_THK-WALL DK GRAY PVC THRD-ONE-END PIPE NIPPLE
4882K110_THICK-WALL DARK GRAY PVC THREADED PIPE NIPPLE x 3
4596K121_THICK-WALL DARK GRAY PVC PIPE FITTING
3795K133_STAINLESS STEEL GAUGE
PI-003
2051K124_CHEMICAL-RESISTANT PVC DUCT
PI-001
5779K638_PUSH-TO-CONNECT TUBE FITTING FOR AIR x 2
5233K520_MASTERKLEER PVC TUBING
PI-004 x 8

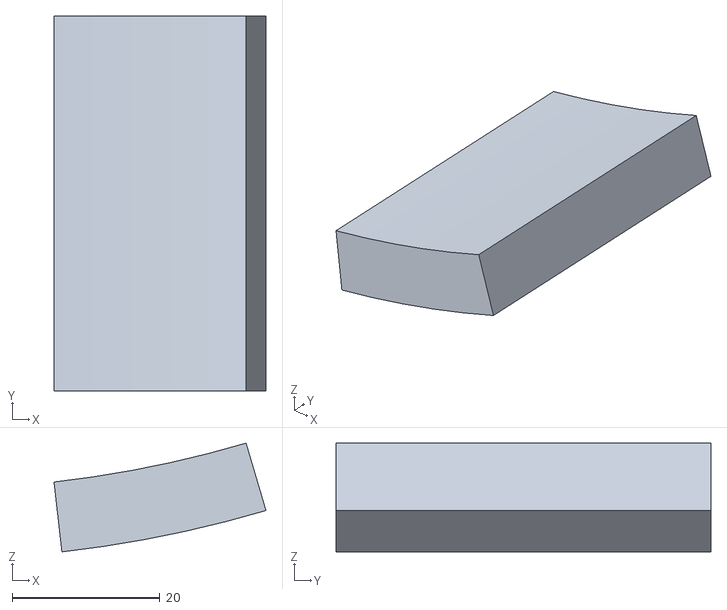
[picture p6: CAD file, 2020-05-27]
HardwareDocumentation/CAD Drawings/STL Files/GA - Bottom assembly-1 PI-004-3.STL
28.7 x 50.8 x 14.7

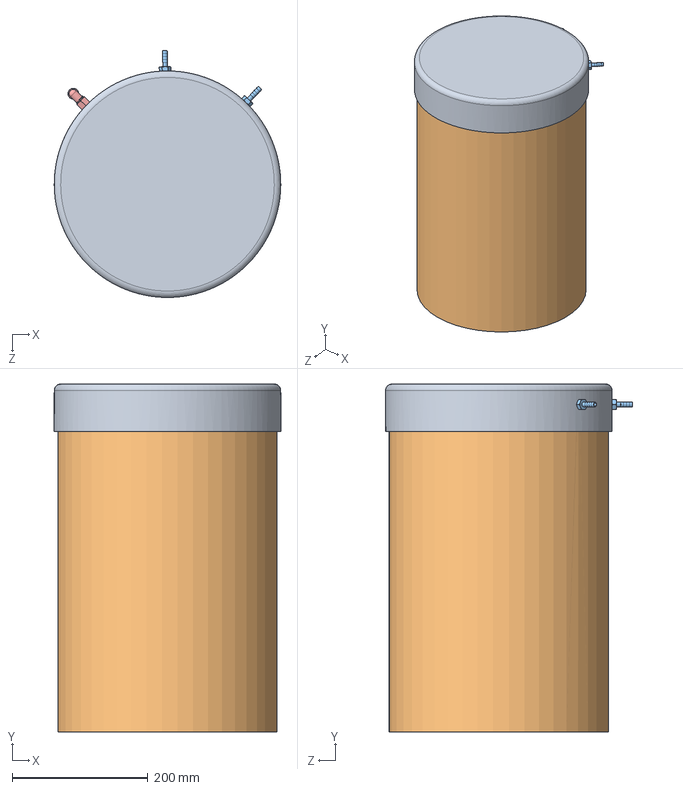
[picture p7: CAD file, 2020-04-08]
HardwareDocumentation/CAD Drawings/SolidWorkds Files/Bottom assembly.SLDASM
333.8 x 512.8 x 363.8 mm
2051K124_CHEMICAL-RESISTANT PVC DUCT
PI-001
5372K112_DURABLE NYLON EXTRA-GRIP BARBED TUBE FITTING x 2
4882K110_THICK-WALL DARK GRAY PVC THREADED PIPE NIPPLE x 2
5779K638_PUSH-TO-CONNECT TUBE FITTING FOR AIR x 2
5233K520_MASTERKLEER PVC TUBING
PI-004 x 8

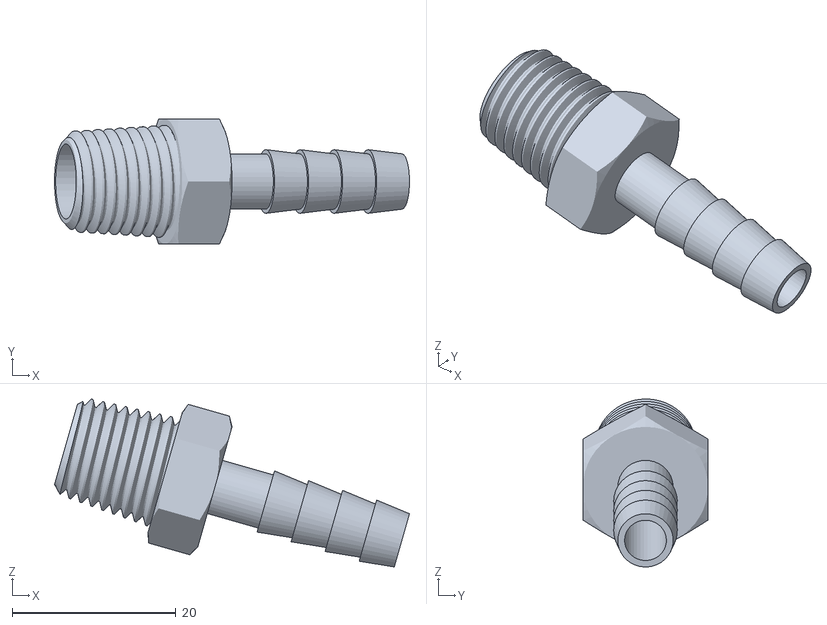
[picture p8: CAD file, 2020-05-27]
HardwareDocumentation/CAD Drawings/STL Files/GA - Bottom assembly-1 5372K112_DURABLE NYLON EXTRA-GRIP BARBED TUBE FITTING-1.STL
43.3 x 15.2 x 20.5

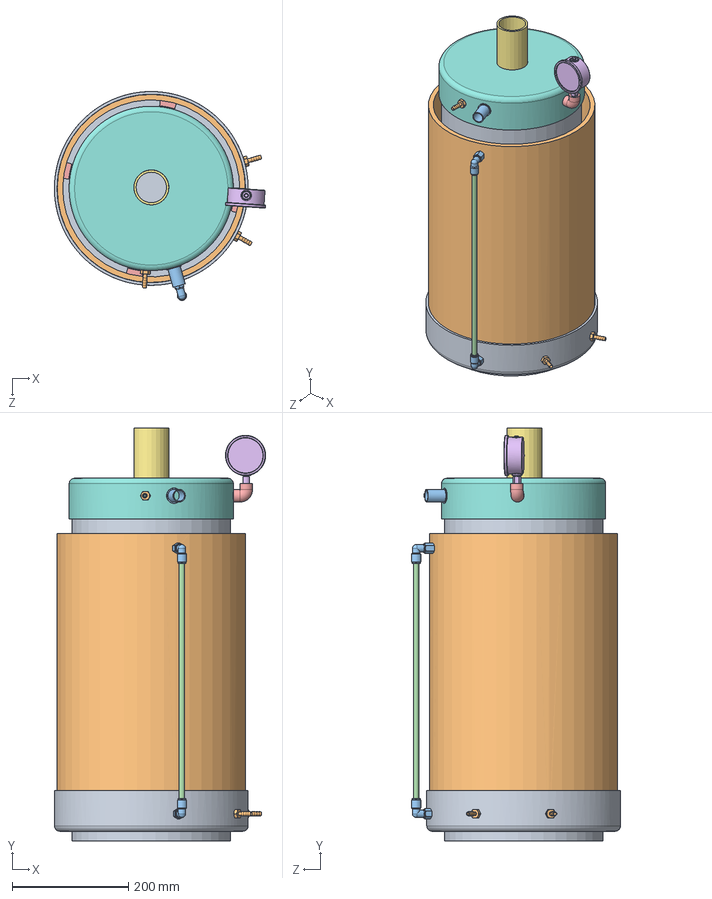
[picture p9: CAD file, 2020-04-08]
HardwareDocumentation/CAD Drawings/SolidWorkds Files/GA.SLDASM
363.8 x 711.2 x 359.9 mm
PI-002
5372K112_DURABLE NYLON EXTRA-GRIP BARBED TUBE FITTING x 3
9173K740_THK-WALL DK GRAY PVC THRD-ONE-END PIPE NIPPLE
4882K110_THICK-WALL DARK GRAY PVC THREADED PIPE NIPPLE x 3
4596K121_THICK-WALL DARK GRAY PVC PIPE FITTING
3795K133_STAINLESS STEEL GAUGE
PI-003
2051K124_CHEMICAL-RESISTANT PVC DUCT - 10inch
2051K124_CHEMICAL-RESISTANT PVC DUCT
PI-001
5779K638_PUSH-TO-CONNECT TUBE FITTING FOR AIR x 2
5233K520_MASTERKLEER PVC TUBING
PI-004 x 8

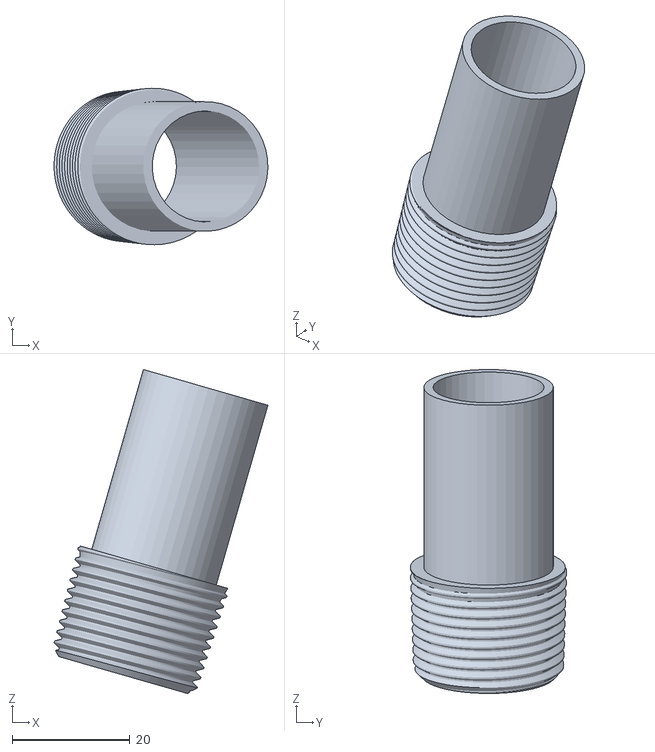
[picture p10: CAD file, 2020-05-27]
HardwareDocumentation/CAD Drawings/STL Files/GA - Top Assembly-1 9173K740_THK-WALL DK GRAY PVC THRD-ONE-END PIPE NIPPLE-1.STL
36.3 x 26.6 x 55.0

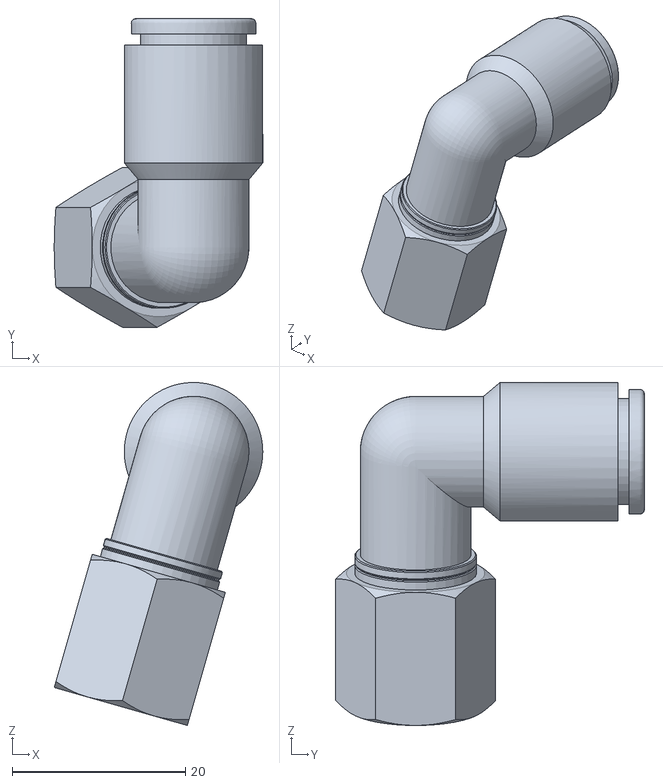
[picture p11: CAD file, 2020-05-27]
HardwareDocumentation/CAD Drawings/STL Files/GA - Bottom assembly-1 5779K638_PUSH-TO-CONNECT TUBE FITTING FOR AIR-2.STL
24.1 x 35.7 x 39.6

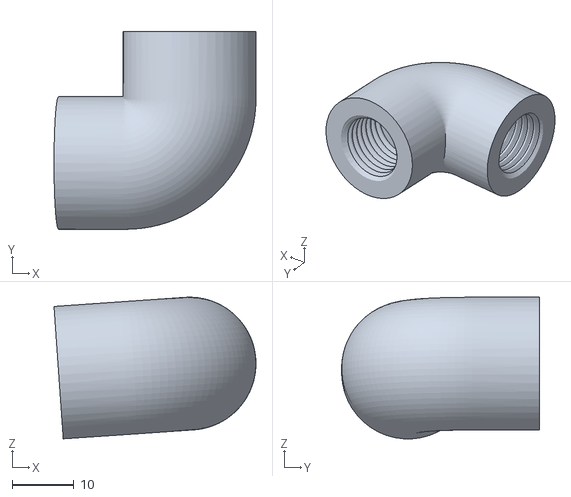
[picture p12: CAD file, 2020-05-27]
HardwareDocumentation/CAD Drawings/STL Files/GA - Top Assembly-1 4596K121_THICK-WALL DARK GRAY PVC PIPE FITTING-1.STL
32.8 x 32.1 x 23.0

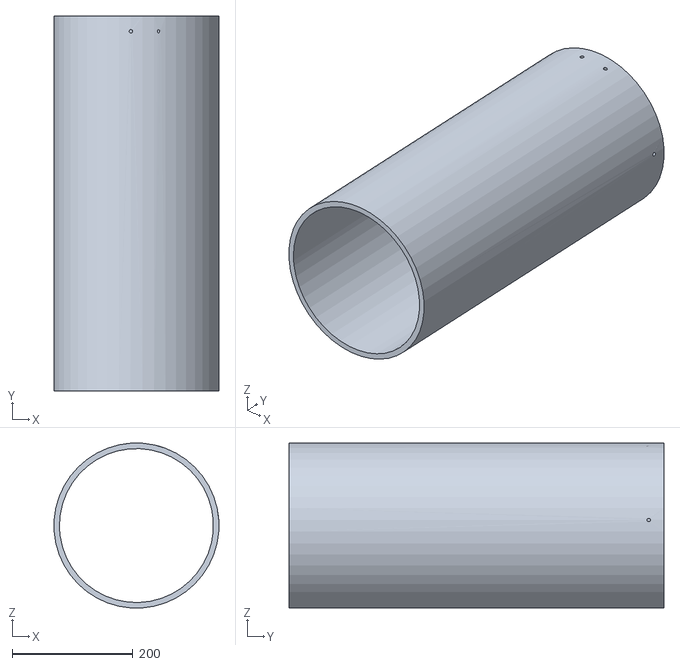
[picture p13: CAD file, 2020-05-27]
HardwareDocumentation/CAD Drawings/STL Files/GA - Top Assembly-1 PI-002-1.STL
272.6 x 620.0 x 272.6

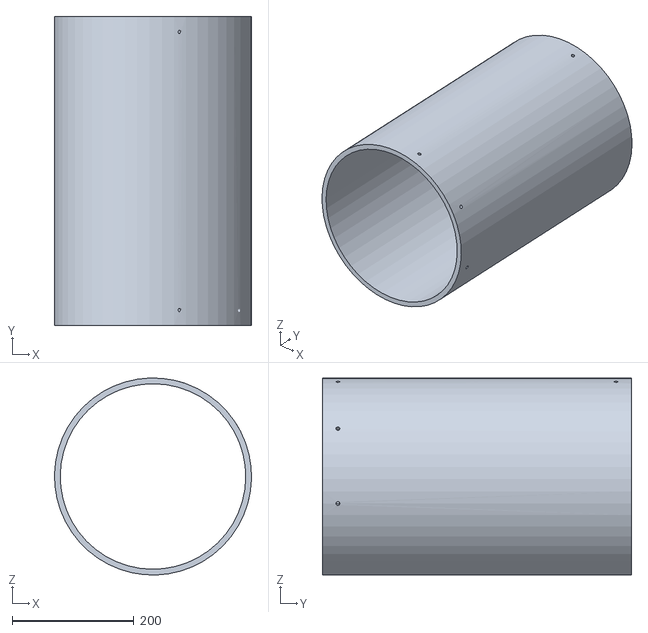
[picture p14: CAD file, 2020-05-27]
HardwareDocumentation/CAD Drawings/STL Files/GA - Bottom assembly-1 PI-001-1.STL
323.7 x 508.0 x 323.6

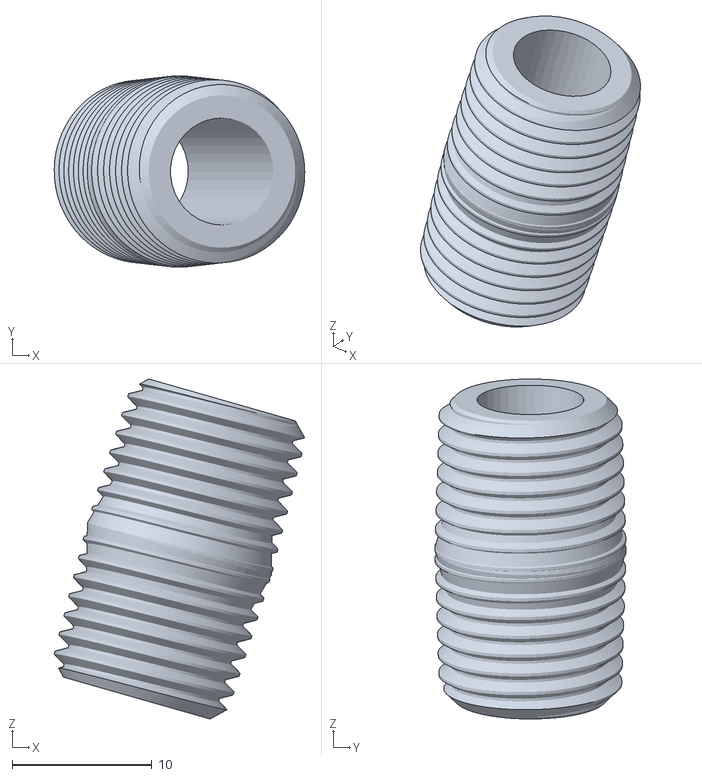
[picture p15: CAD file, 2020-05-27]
HardwareDocumentation/CAD Drawings/STL Files/GA - Bottom assembly-1 4882K110_THICK-WALL DARK GRAY PVC THREADED PIPE NIPPLE-1.STL
18.0 x 13.7 x 24.4

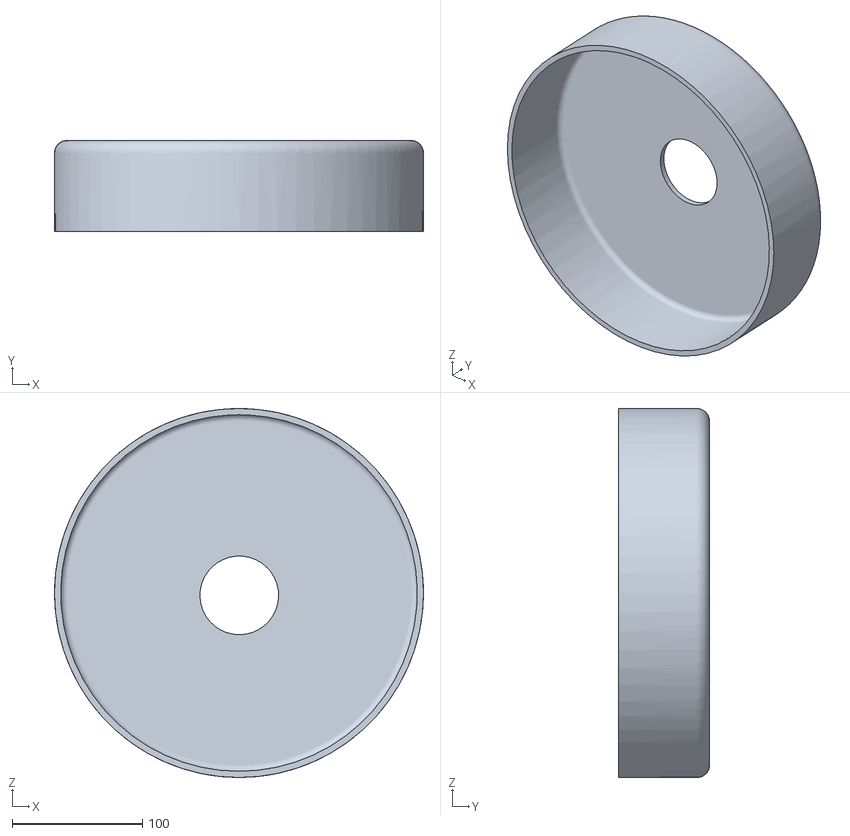
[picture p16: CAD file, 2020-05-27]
HardwareDocumentation/CAD Drawings/STL Files/GA - Top Assembly-1 2051K124_CHEMICAL-RESISTANT PVC DUCT - 10inch-3.STL
283.0 x 69.8 x 283.0

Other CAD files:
HardwareDocumentation/CAD Drawings/STL Files/GA - Bottom assembly-1 PI-004-13.STL
HardwareDocumentation/CAD Drawings/STL Files/GA - Bottom assembly-1 2051K124_CHEMICAL-RESISTANT PVC DUCT-1.STL
HardwareDocumentation/CAD Drawings/STL Files/GA - Bottom assembly-1 PI-004-4.STL
HardwareDocumentation/CAD Drawings/STL Files/GA - Top Assembly-1 PI-003-1.STL
HardwareDocumentation/CAD Drawings/STL Files/GA - Bottom assembly-1 4882K110_THICK-WALL DARK GRAY PVC THREADED PIPE NIPPLE-2.STL
HardwareDocumentation/CAD Drawings/STL Files/GA - Bottom assembly-1 5372K112_DURABLE NYLON EXTRA-GRIP BARBED TUBE FITTING-2.STL
HardwareDocumentation/CAD Drawings/STL Files/GA - Bottom assembly-1 5779K638_PUSH-TO-CONNECT TUBE FITTING FOR AIR-1.STL
HardwareDocumentation/CAD Drawings/STL Files/GA - Bottom assembly-1 PI-004-1.STL
HardwareDocumentation/CAD Drawings/STL Files/GA - Bottom assembly-1 PI-004-14.STL
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

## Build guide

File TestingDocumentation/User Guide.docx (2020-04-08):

User Guide

How it works:

The basis of this system is gravity, water and two PVC pipes to create an inherently pressure controlled system capable of ventilation. Each pipe is sealed at one end, the outside pipe is closed at the bottom, with a smaller diameter pipe inverted inside it and open at its base. Water in the system allows a seal to be made between the two pipes. By introducing air into the system, the top pipe is displaced upwards from its resting position. The water seal prevents it’s escape and we create a storage of pressure. The created pressure is a result of the weight of the system pushing the water column downwards, and subsequently, the water column’s equal upward force on the trapped air.

Air is supplied by a constant flow of gas coming from the hospital’s outlet. The hospital tubing is attached to a nipple on the top of the inner PVC pipe (a ¼” fitting required for hospital tubing).

Air/O2 builds up in the system and once the valve to the patient is opened, it is released through a port to the intubated patient. This valve is controlled on an electronic circuit, which gives the operator the ability to control respiratory rate, I:E ratio and amount of volume delivered to the patient. When the valve is closed, air volume builds in the system, and the inner pipe slowly rises. When the valve is open, the net flow of air is out of the system (air flow in<air flow out) and the inner pipe falls.

The pressure in the system is dictated by the total weight of the inside pipe, and can be modulated by adding weights to the top of the system to gain higher pressures. The total surface area of the water column being pushed down in this specific system is 478cm². Therefore, adding 478g to the top of the system will displace 486ml of water 1 cm, and increase the total pressure by 1cm H2O.

The overall weight of the system does not change significantly with a drop in height of the inner pipe (ignoring buoyancy forces on the pipe that used to be out of the water and is now underwater). Now that we know pressure is a result of weight, we know that the pressure will not change significantly with a drop in height either. It is only the volume of the trapped air that changes significantly. Thus, this system can be thought of as an air flow capacitor, storing extra air molecules but without making them significantly more compressed as more are added.

Link to youtube videos explaining our concept on a previous prototype:

1) Concepts

https://youtu.be/Rif06Y2mUV0

2) Design + components

https://youtu.be/FJwJgYTQQ7E

3) Demonstration

https://youtu.be/cVoM8isjuaQ

4) Gravity Ventilator in action

https://vimeo.com/402755875/e5e537c527

Setup:

There is a small diameter (2”) PVC pipe running through the inside pipe and is open to the air, which allows for excess Air/O2 to escape the system in a controlled manner.

This system is designed to provide a breath to the patient with a constant and sustained pressure (stable plateau pressure). A manometer is connected to the inside pipe which provides constant feedback of the pressure within the system.

We have a sight glass set up that allows us to visualize the volumes delivered to the patient (though this is not necessary in a final model). This also allows us to visualize how much water is in the system.

As there is interaction between the air delivered to the patient and the water within the system, we have the water in the system sterilized by a UV light pump system at 23mcgW/cm². This filtration system is attached to the bottom of the outer PVC pipe.

Though not installed in this system, we will place a spout at the base of the system, to allow for easy drainage of the water from the system.

To set up the system, connect all tubing as detailed in the assembly guide. The UV light/pump and the circuit board need to be plugged into a standard wall plug. Add ~8L of water to the outer pipe (filled until approximately 5cm high on the sight glass). To start the system, set the respiratory rate and I:E ratio on the circuit and turn the wall O2/air blender onto 8-10L/min. The system should start running and deliver breaths to the patient at the rate you set on the circuit. To change the pressure, add or remove weight from the top of the ventilator (there is a tube coming out of the top of the ventilator that holds the weight). Adding 478g increases the pressure by 1cm H20.

Operation:

There are two modes of operation that can be used with this ventilator:

Volume Control Mode: provides consistent tidal volumes at regular intervals for patient breathing, given adjustable breaths per minute and inspiratory/expiratory time ratio.

Pressure Control Mode: allows the patient to trigger a new mechanical breath during expiration, given a variable mandatory breath rate and trigger pressure threshold.

To turn on the ventilator:

1. Connect the ventilator to the power source. Display should show ‘Ventilator OFF’.
2. Use the slide switch to select desired operation mode:
  a. Volume Control Mode
  b. Pressure Control Mode
3. Turn the knobs to adjust for the desired parameters of the selected operation mode as shown in the table below:

Knob | Timing Mode | Pressure Control Mode
1 | Inspiration/Expiration Ratio (Range: 1:1 – 1:5) | Max Time Before Inhale (Range: 750 – 6000ms)
2 | Breaths per Minute (BPM) (Range: 5 – 40) | Inhalation Trigger Pressure Threshold (Range: -4 – -1 cmH2O)
3 | N/A | Max Time Before Exhale (Range: 750 – 6000ms)

*Note: parameters can only be adjusted while the ventilator is off.

4. Press the button labelled Start/Stop to turn on the ventilator. Display should show ‘Ventilator ON’.

To turn off the ventilator:

WARNING: follow the following steps to safely disconnect a patient from the ventilator. Doing so will allow the air in the system to pass through a filter before being expelled.

1. Step 1 - Turn off Ventilator
2. Step 2 - Turn off Source Flow
3. Step 3 - Disconnect Patient by disconnecting the HME from Ventilator Circuit, keeping HME attached to ETT - Direct circuit into gauze while pressure and flow from gravity chamber is released.
4. Step 4 - Begin Manual ventilation to support patient.

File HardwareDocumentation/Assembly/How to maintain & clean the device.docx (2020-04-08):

Maintenance and cleaning of the device

This majority of the components of the main ventilator system are assembled with unplasticised PVC, an inert, chemically resistant substance. Insertion of parts can be accomplished through plastic welding, PVC glue or friction fitting with teflon tape. All of these are suitable for drinking water purposes.

The only interface between air going to the patient and the outside environment is through the water in the system. As this leads to the small potential for contamination in the system, this water is constantly cleaned and sanitized throughout the use of the ventilator, by using an external pump and UV sterilizer. This runs a 9W bulb and sterilizes water at 23mcgW/cm². This ensures inhibition of bacterial, fungal and some viral growth within the water reservoir.

Between use, the device should be cleaned in accordance with hospital protocols. The best method of sterilizing unplasticized PVC is Ethylene Oxide Sterilization, though this is not widely available (available at VGH in the lower-mainland of B.C.). An alternative can be a thorough wipe down with ethanol or iodophor. All tubing will be sanitized or replaced in accordance with hospital policy.

LINK TO FULL DEMONSTRATION VIDEO: https://vimeo.com/402801085/5c2932b0c2

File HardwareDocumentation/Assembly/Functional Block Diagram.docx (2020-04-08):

Functional Block Diagram

Current Prototype:The current prototype is a mass powered pressure chamber with a water seal. This system is capable of providing a constant inspiratory pressure with a built-in pressure limit. An oxygen blender provides the range of FiO2 settings, while a flowmeter provides the flow that pressurizes the gravity chamber. A solenoid alternates between the pressure chamber and the PEEP Valve, allowing for set inspiratory and set expiratory pressures. A microcontroller with analog interface allows for modification of Respiratory Rate and I:E Ratio. An HME filters expired air, keeping components free from secretions and other gross soiling, while providing passive heat and humidification.

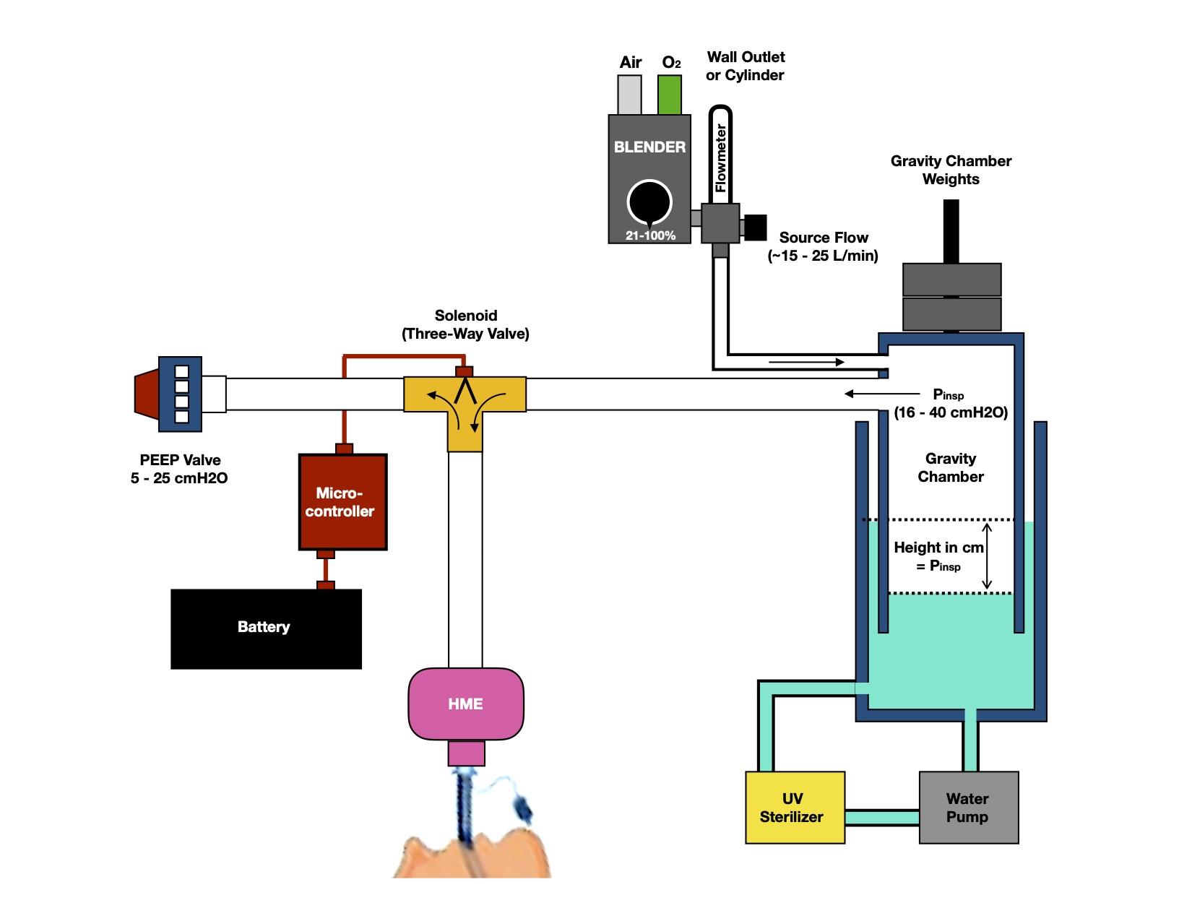
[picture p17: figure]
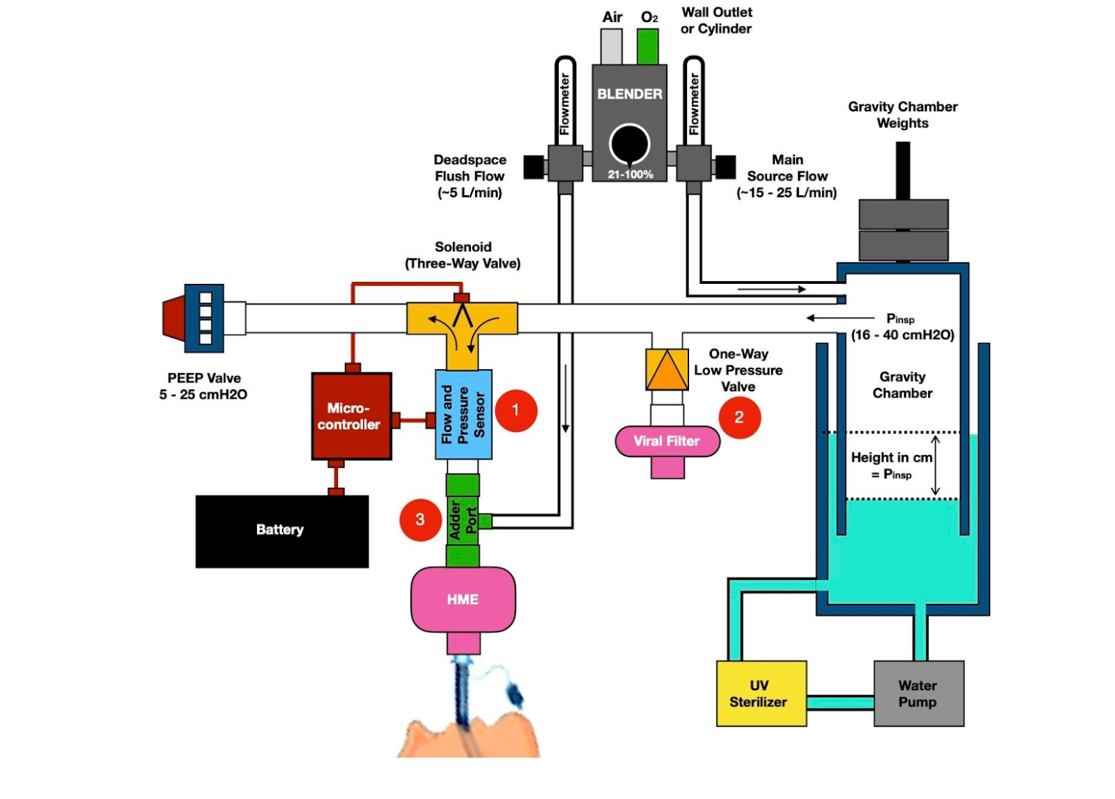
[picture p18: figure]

Near Future Additions: There are three planned essential additions that will improve the functionality and safety of this device.

1. The addition of a flow and pressure sensor will allow for pressure, volume, and flow monitoring, but also allow for sensing patient efforts. This will also allow for the inclusion of important volume and pressure alarms.
2. A one-way check valve will allow the patient to draw room air during the inspiratory phase in the event of a loss of pressure. This safety feature will prevent a possible draw of fluid from the gravity chamber into the breathing circuit. A filter ensures no contamination by air drawn from the room.
3. Given the single limb nature of the circuit, dead space will be an issue, and providing a flush flow will reduce rebreathing and also provide a flow to draw upon when triggering the ventilator.

We are awaiting delivery of parts that will allow us to incorporate these changes, and code has been written to integrate flow and pressure measurements.

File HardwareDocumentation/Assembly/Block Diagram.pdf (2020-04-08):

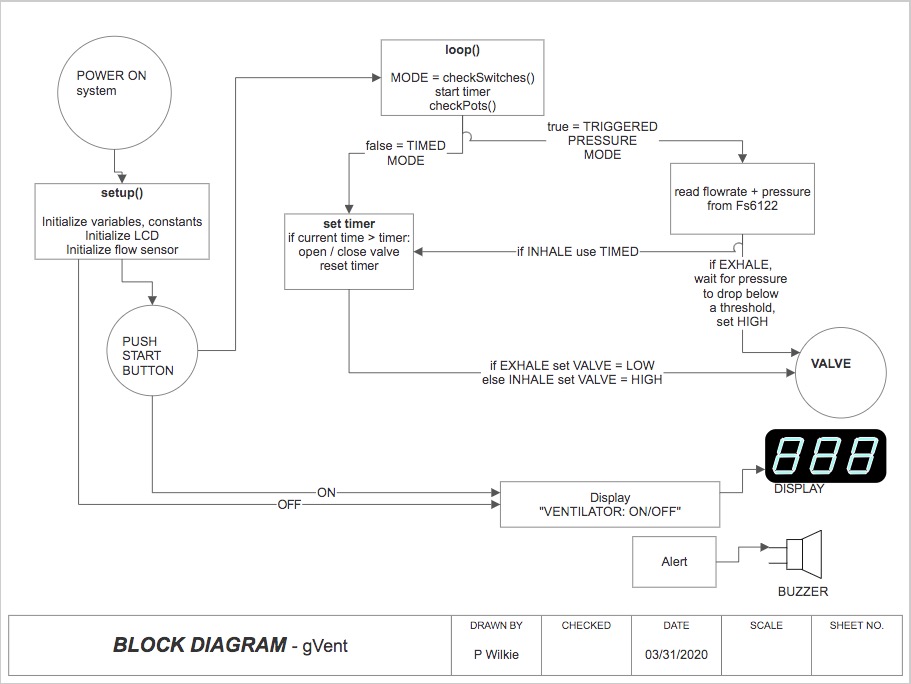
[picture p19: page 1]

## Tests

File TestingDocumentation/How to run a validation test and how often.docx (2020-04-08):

gVent Validation Testing

Prior to connecting a patient to the ventilator a simple verification test should be complete to confirm no faults in the system. For a patient being maintained on this device for mechanical ventilation, a ventilator check should be completed regularly. Although there is no verified national standard, regular ventilation checks in the ICU are recommended to occur every 4 hours by the Society of Critical Care medicine (1). Further testing of our device specifically is needed to determine if we would need ventilation checks at a higher frequency than the recommended standard.

To conduct a validation test the following would be checked prior to connecting a patient to the ventilator:

1) Validate and calibrate pressure settings
  a) Our design currently has an external water column for visualization of pressures generated by the water column inside the canister, as well as a manometer placed near the top of the internal column.
  b) Simply cross comparing the pressure readouts of these two devices provides a means of cross comparing that the pressure within the canister is that which is expected.
  c) By connecting an in-line manometer to the circuit after the valves and more proximal to the patient, we could confirm the discrepancy between intended pressures as indicated on the ventilator manometer and those more proximal to the patient subject to resistance of the circuit.
  d) Although not currently included due to delays in supply, a pressure sensor will be enclosed with our flow sensor.
  e) The pressure sensor would be calibrated ahead of each use by turning off source flow, opening all out flow ports, and then closing all outflow ports to create a depressurized and closed circuit. We would then occlude the patient port and zero the pressure sensor.
2) Verify volume delivered
  a) Final designs are inclusive of a flow sensor that would be calibrated and enable us to have ongoing feedback about volume of gas flow. Given delays in supply we do not yet have the flow sensor to incorporate into our working model and so propose the alternative means of verifying the delivered volume of gas.
  b) The flow sensor would be calibrated ahead of each use by turning off source flow, opening all out flow ports, and then closing all outflow ports to create depressurized and closed circuit with zero flow. We would then occlude the patient port and zero the flow sensor.
3) Verify pressure release mechanism
  a) As designed, the system is inherently pressure limited and so the point at which this bubbling begins indicates the maximum pressure it could administer, as limited by the weight of the upper column.
  b) To confirm this inherent safety mechanism is limited to a pressure of 40cm of H2O, occlude patient outflow and pressurize the system to a point where bubbling occurs in the canister.
  c) Hold pressure here and confirm that 1) alarm sounds when exceeding a pressure of 40cm H20 and 2) excess pressure is being released through bubbling.
4) Verify low pressure alarm
  a) Turn main source flow off, and open the patient port on inspiratory phase to depressurize the gravity chamber. Set Ventilator to pause on expiratory phase. Adjust PEEP Valve to 25 cmH20. Turn Dead Space Washout Flow to 10L/min.
  b) Occlude patient port and pressurize system to 25 cmH20.
  c) Set Low Pressure Alarm to 10 cmH20.
  d) Slowly adjust PEEP Valve down in increments of 5 cmH20 until alarm sounds.
  e) Verify that the PEEP Valve is set to 10 cmH20 (or within a 10% error) as the PEEP represents the only pressure in the system in this setting, and we have set the alarm to sound at a threshold of 10cm H20.
5) Verify low and high minute ventilation alarms
  a) Once a flow sensor is included in the design we will be able to detect tidal volumes, combined with the respiratory rate this will provide us with the minute ventilation.
  b) Inclusive in our code is an alarm to sound when the minute ventilation is above or below the parameters set for the specific patient, roughly a minimum would be to alarm at half the desired minute ventilation and a high would alarm at approximately double the patient’s desired minute ventilation.
6) Circuit Leak Test
  a) Occlude patient port, then pressurize the system to 40 cmH20. Turn off Source Flow (and once added, Dead Space Washout Flow). Observe the pressure chamber for 5 minutes to ensure no gross loss of volume. Ensure during this time, flow measurement remains at 0 L/min. Open the patient port and resume source gas flow.
1. Mechanical Ventilation in Adult Patients with Acute Respiratory Distress Syndrome - Am J Respir Crit Care Med. 2017 May 1;195(9):1253-1263

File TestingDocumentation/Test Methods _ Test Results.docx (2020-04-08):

gVent Testing Methods & Test Results

Prototype 3 of the gVent was tested over a 2.5 hour period throughout which it was cycling continuously, at various ventilation parameters. It performed reliably through the duration of the testing session.

Pressures - Testing maximum and minimum

To test maximum and minimum pressures we used a manometer connected to the upper portion of the inner cylinder of the gravity ventilator, correlated for validation to the externalized water column representative of internal pressures. We did not have access to a pressure gauge to place distal in the circuit but would conduct further testing to confirm pressures more proximal to the patient.

Minimum inspiratory pressure - 16cm H2O

This is limited by the weight of the upper cylinder as it is essentially the weight of the upper cylinder, as indicated on the manometer the minimum pressure was 16cm H20. Lower pressures could be achieved through further manufacturing of a lighter upper cylinder.

Maximum inspiratory pressure - 40cm of H2O

This was recorded by adding weights to the upper cylinder. At this point, the water seal gave way and pressure was released through bubbling. Given that 40cm of H2O is the upper limit of a clinically safe inspiratory pressure this is a desirable feature. However, theoretically, we could reach a high maximum pressure by increasing the amount of water used to fill our cylinder.

The system is currently designed as a 1 way non-rebreathing circuit. Therefore, maximum positive end expiratory pressure (PEEP) is simply controlled by putting the distal end of the exhaust tubing under controlled pressure. By placing an AMBU bag PEEP valve on the distal end of the exhaust tubing set to 25cm H2O we were able to confirm the system’s ability to hold a pressure in the test lung. This was only confirmed visually as we did not have access to an inline manometer at the time of testing.

Flow - Testing maximum and minimum

To test maximum flow, the system was set at a RR of 13, with an I:E ratio of 1:1 with near maximum driving pressures at 39cm of H20. The circuit was connected to a flowmeter that read out both flow and tidal volumes.

With these parameters a maximum tidal volume of 1.955 L and maximum flow of 56.05 SLP was recorded.

At this time we are very pleased with these values and feel our greatest limiting factor is the small diameter of our current solenoid valve (¼”).

Time to repressurize the system

This test was completed by depressurizing the system completely by exposing the outflow port to room air, then reconnecting the circuit to the flowmeter in the testing environment. We confirmed the starting pressure was 0 cmH20 on the manometer and then filled the system with an inflow of 15L/min. We measured the elapsed time to reach a pressure of 25 cm of H2O as indicated on the manometer attached to the cylinder.

As per our testing, it would take 5.25s to pressurize the column from 0cmH20 to 25cm H20 with hospital wall inflow oxygen governed at a maximum of 15 L/min.

Respiratory rate

By increasing the commanded respiratory rate we can test the upper limit.

The system has shown the capability to run at a respiratory rate of 40 bpm. The minimum of 6 bpm can also be easily achieved and maintained by the system. Currently our code is set to enable a range of 5-50bpm, this range is easily adjusted by changing the values entered in the code.

I:E Ratio

Included in our code is an adjustment of I:E ratio from 1:1 through to 1:5. We successfully tested the ability to program and run the system on all four settings.

Confirming adequate water volumes

The system relies on a water column within the two cylinders, therefore we must ensure there is an appropriate volume of water to drive the system. The system can accommodate a large range of water volumes but inherent in the design the system will 1) bottom out when the water volume is too low to meet the pressure demands and 2) bubble over if the water level is too high to accommodate the increased volume of the cylinder descending into the water column. More concisely, the system simply would not operate if the water level was not sufficient.

Confirming FiO2

The system is not currently sensing gas composition. If the supply was purely wall oxygen we would expect the FiO2 to be 100%. We could mix this with room air to decrease incrementally. An oxygen sensor would need to be placed in the circuit to record the actual FiO2, this would be a meaningful addition.

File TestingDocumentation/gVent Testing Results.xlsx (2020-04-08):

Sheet: Test Results
gVent Testing
black features are those required for non-ICU ventilators: https://buyandsell.gc.ca/sites/buyandsell.gc.ca/files/non-icu-ventilator-requirements_0.pdf
blue features are those speficied for ICU ventilators: https://buyandsell.gc.ca/sites/buyandsell.gc.ca/files/ventilatorspecs2020covid19outbreak.pdf - Refer to this document for comprehensive list, not all criteria included here
Test Date | 2020-03-31 | 2020-04-09
Prototype | 3 | 4
 | no P/flow sensors | P/flow sensors inclusive
Capabilities re: Ventilator Modes
Controlled ventilation with:
pressure control | yes
volume control | -
Pressure Support | -
Synchronized intermittent mechanical ventilation (SIMV) - essentially PC or VC + PS | -
Back up ventilation 2º to low MV | -
Ventilator Parameters
FiO2 21-100% | -
PEEP range (Goal 0-30; 35cm H2O) | 0-25
Pressure support beyond PEEP (Goal of 60cm H2O) | -
Maximum Flowrate (goal 100; 150 SLP) | 56.05
Max Tidal Volume (goal of 1500ml;2000ml) | 1.955
Maximum Resp Rate (goal 45 bpm;150bpm) | 60
I:E Ratio Range (goal 1:1 - 1:4) | 1:1 - 1:5 | 1:1 - 1:5
Peak Inspiratory Pressure (80cm H2O) | 40
Minimum Inspiratory Pressure | 16
Inspiratory Time (Goal 0.1-5s) | -
Inspiratory rise time (0-.4s) | -
Flow trigger sensitivity (tested threshold) | -
Prssure trigger sensitivity (tested threshold) | -
Alarms (45-85dBA)
Peak Pressure
High | -
Low | -
Tidal Volume (optional for non-ICU)
High | -
Low | -
Respiratory Rate (optional for non-ICU)
High | -
Low | -
Minute Ventilation (TV*RR)
High | -
Low | -
FiO2
High | -
Low | -
PEEP
High | -
Low | -
Apnea alarm with back up rate & TV | -
Disconnection alarm
Extra considerations
Safety Relief Valve | Pressure limited at 40cmH20
Plateau Pressure Readings
Ability to connect various vent circuits?
Dispay/touch screen (all only for ICU vent)
Vent mode & breath type
Delivered FiO2
Airway pressures:
Peak
Mean
Plateau
PEEP
Respiratory Rate
TV
MV
I:E Ratio
Graphing of:
Pressure vs t
Flow vs. t
Volume vs. t
Flow/volume loops

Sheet: Sheet2
https://www.gov.uk/government/publications/coronavirus-covid-19-ventilator-supply-specification/rapidly-manufactured-ventilator-system-specification
Ventilation
At least 1, optionally 2 modes of ventilation:
must have mandatory ventilation (for the deeply sedated and paralysed). The user can set a tidal volume and the output is a pressure regulated flow to achieve this volume, for example, pressure regulated volume control (PRVC), SIMV-PC
optional pressure support mode for those patients breathing to some extent themselves, for example, BIPAP. The user sets an inspiratory pressure and an expiratory pressure. The ventilator can sense when a patient starts to breathe in and apply the inspiratory pressure, then sense when the patient starts to breathe out and apply the expiratory pressure (this pressure is still positive but lower than the inspiratory pressure)
If the patient stops breathing in pressure support mode, it must failsafe automatically onto mandatory ventilation.
Inspiratory airway pressure, the higher pressure setting that is applied to make the patient breathe in:
plateau pressure should adapt to achieve volume and be limited to 35 cmH2O
peak pressure should be no more than 2 cmH2O greater than plateau pressure
ideally there should be a mechanical failsafe valve that opens at 40 cmH2O
Positive End Expiratory Pressure PEEP (usually called EPAP during pressure support mode). The lower pressure applied to the patients airway to allow them to breathe out, but not too much:
range 5 to 25 cm H2O adjustable in 5 cmH2O increment
patient breathing system must remain pressurised to at least the PEEP level setting at all times
Inspiratory:Expiratory ratio (I:E) (note, confusingly, it is actually E/I time). The proportion of each breathing cycle that is spent breathing in compared to breathing out:
2.0 (i.e. expiration lasts twice as long as inspiration)
optionally adjustable in the range 1.0 to 3.0
Respiratory Rate. The number of breathing cycles every minute:
range 10 to 30 breaths per minute in increments of 2 (only in mandatory mode) can be set by the user
Tidal Volume (Vt). The volume of gas flowing into the lungs during one inspiratory cycle:
must have at least one setting of 400ml +/- 10 ml
ideally 350ml and 450 ml options
optionally Range 250 to 600 ml in steps of 50ml
even more optionally up to 800 ml
optionally the ability to input body weight and have volume calculated as, for example, 6ml/kg of ideal body weight

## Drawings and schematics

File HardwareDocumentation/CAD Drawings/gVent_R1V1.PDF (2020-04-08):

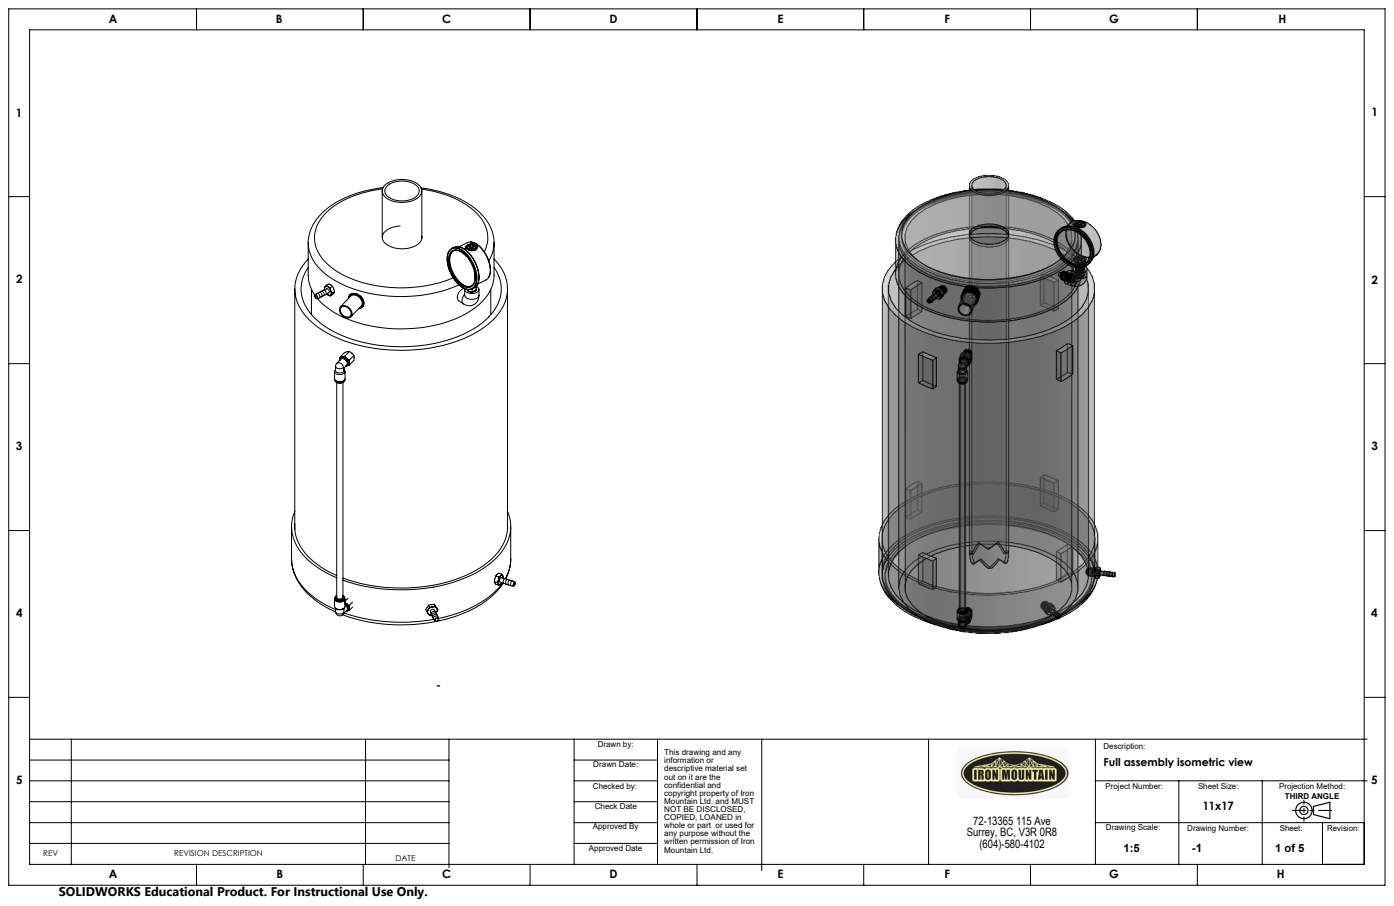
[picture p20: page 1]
Drawn Date:; 72-13365 115 Ave Surrey, BC, V3R 0R8; Sheet Size:; Projection Method:; THIRD ANGLE; Drawn by:; Checked by:; Check Date

Description:
Full assembly isometric view
5 Project Number:

This drawing and any
information or
descriptive material set
out on it are the
confidential and
copyright property of Iron
Mountain Ltd. and MUST
NOT BE DISCLOSED,
COPIED, LOANED in
whole or part or used for
any purpose without the
written permission of Iron
Mountain Ltd.

Approved By | | | Drawing Scale: 1:5 | Drawing Number: -1 | Sheet: 1 of 5 | Revision:

REVISION DESCRIPTION | DATE REV | Approved Date

SOLIDWORKS Educational Product. For Instructional Use Only.

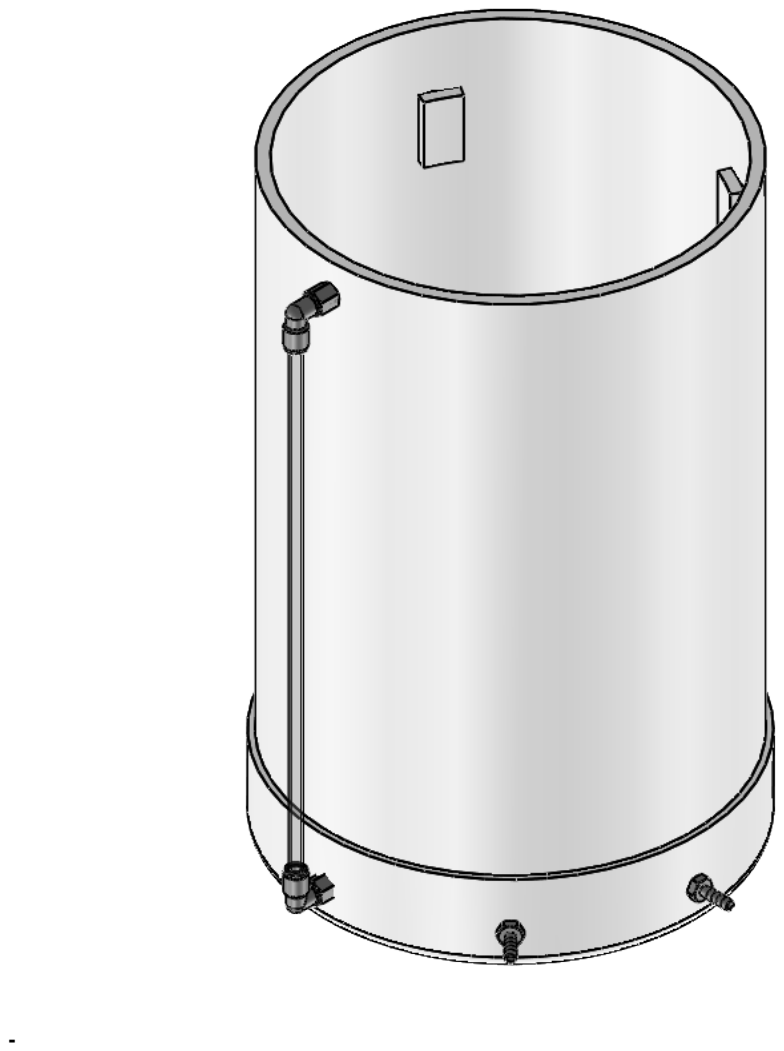
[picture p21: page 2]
Drawing Scale:; Drawn Date:; 72-13365 115 Ave; Sheet Size:; Projection Method:; THIRD ANGLE; Drawing Number:; Sheet:; Revision:; Drawn by:; Checked by:; Approved By; Check Date

Description:
Bottom assembly isometric view
5 Project Number:

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

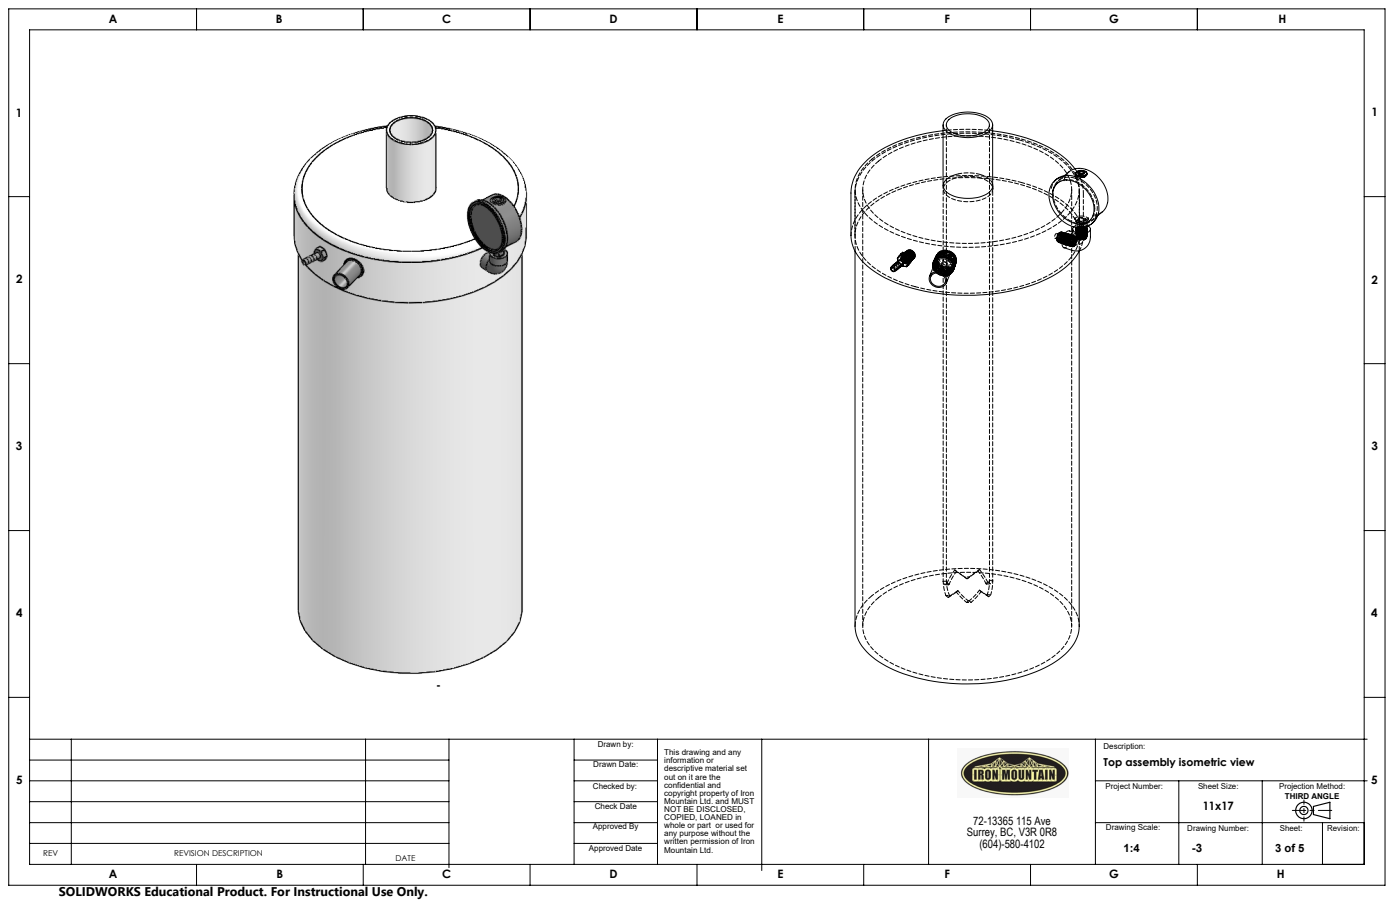
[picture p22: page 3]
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

Description:
Top assembly isometric view
5 Project Number:

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

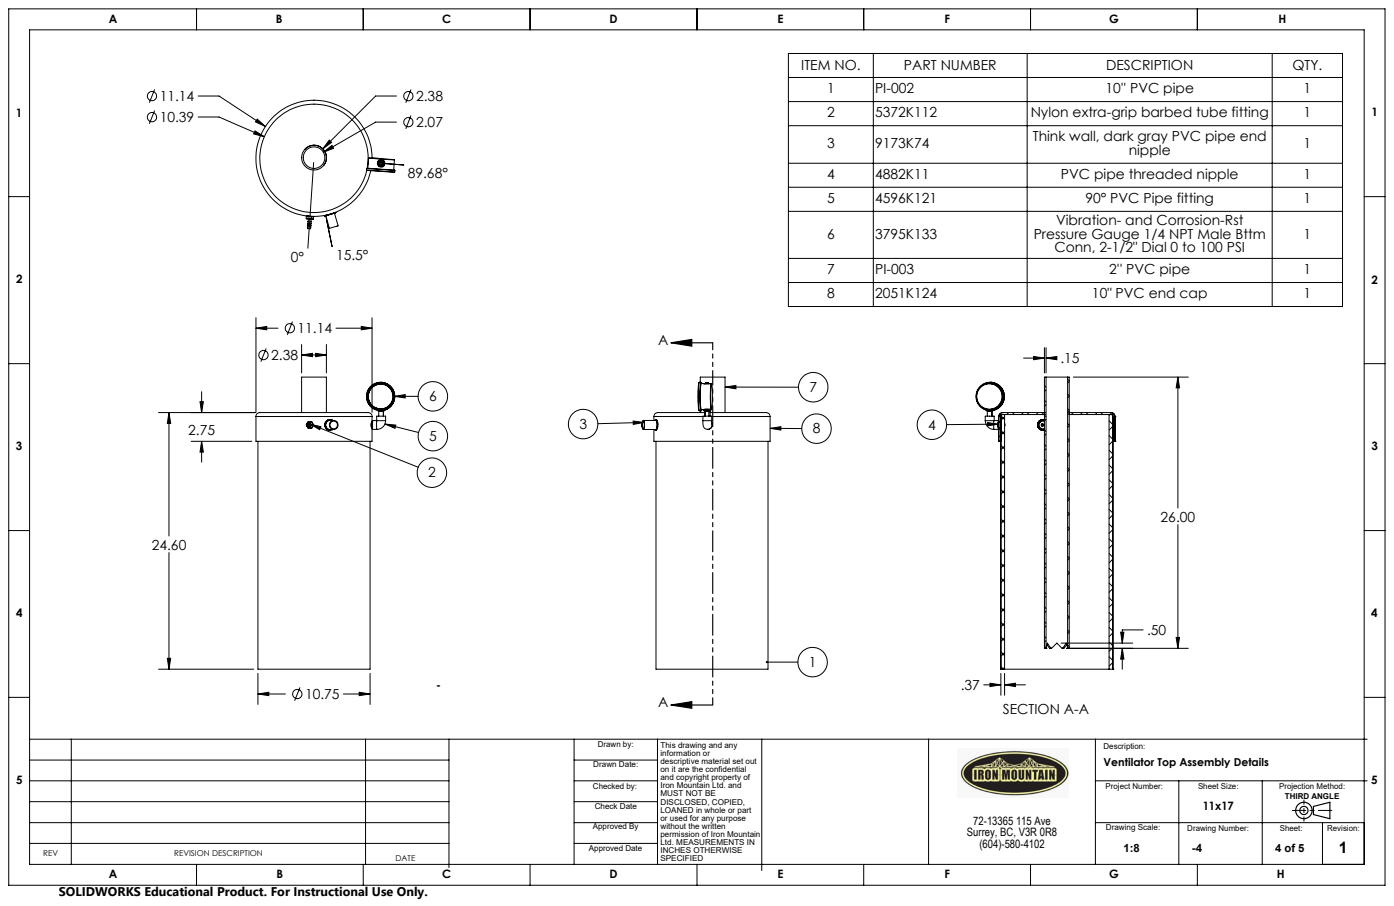
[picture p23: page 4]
SECTION A-A; Drawing Scale:; Drawn Date:; 72-13365 115 Ave; Sheet Size:; Projection Method:; THIRD ANGLE; Drawing Number:; Sheet:; Revision:; Drawn by:; Checked by:; Approved By; Check Date

ITEM NO. | PART NUMBER | DESCRIPTION | QTY.
1 | PI-002 | 10'' PVC pipe | 1
2 | 5372K112 | Nylon extra-grip barbed tube fitting | 1
3 | 9173K74 | Think wall, dark gray PVC pipe end nipple | 1

4 | 4882K11 | PVC pipe threaded nipple | 1
5 | 4596K121 | 90° PVC Pipe fitting | 1
6 | 3795K133 | Vibration- and Corrosion-Rst Pressure Gauge 1/4 NPT Male Bttm Conn, 2-1/2" Dial 0 to 100 PSI | 1

7 | PI-003 | 2'' PVC pipe | 1
8 | 2051K124 | 10" PVC end cap | 1

This drawing and any
information or
descriptive material set out
on it are the confidential
and copyright property of
Iron Mountain Ltd. and
MUST NOT BE
DISCLOSED, COPIED,
LOANED in whole or part
or used for any purpose
without the written
permission of Iron Mountain
Ltd. MEASUREMENTS IN
INCHES OTHERWISE
SPECIFIED

Description:
Ventilator Top Assembly Details
5 Project Number:

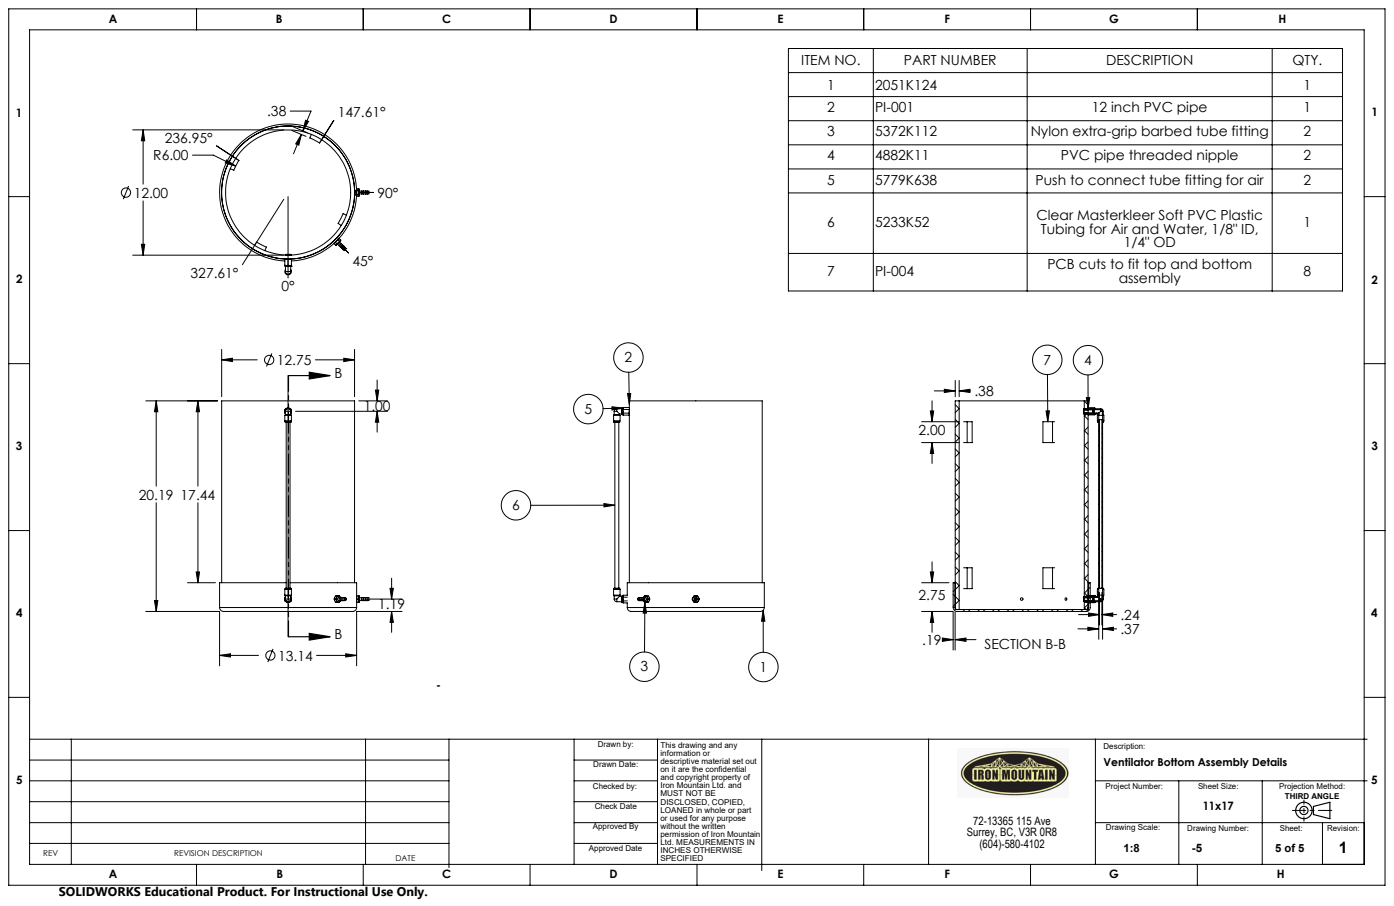
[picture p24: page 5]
SECTION B-B; Drawing Scale:; Drawn Date:; 72-13365 115 Ave; Sheet Size:; Projection Method:; THIRD ANGLE; Drawing Number:; Sheet:; Revision:; Drawn by:; Checked by:; Approved By; Check Date

ITEM NO. | PART NUMBER | DESCRIPTION | QTY.
1 | 2051K124 | | 1
2 | PI-001 | 12 inch PVC pipe | 1
3 | 5372K112 | Nylon extra-grip barbed tube fitting | 2
4 | 4882K11 | PVC pipe threaded nipple | 2
5 | 5779K638 | Push to connect tube fitting for air | 2
6 | 5233K52 | Clear Masterkleer Soft PVC Plastic Tubing for Air and Water, 1/8" ID, 1/4" OD | 1

7 | PI-004 | PCB cuts to fit top and bottom assembly | 8

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

Description:
Ventilator Bottom Assembly Details
5 Project Number:

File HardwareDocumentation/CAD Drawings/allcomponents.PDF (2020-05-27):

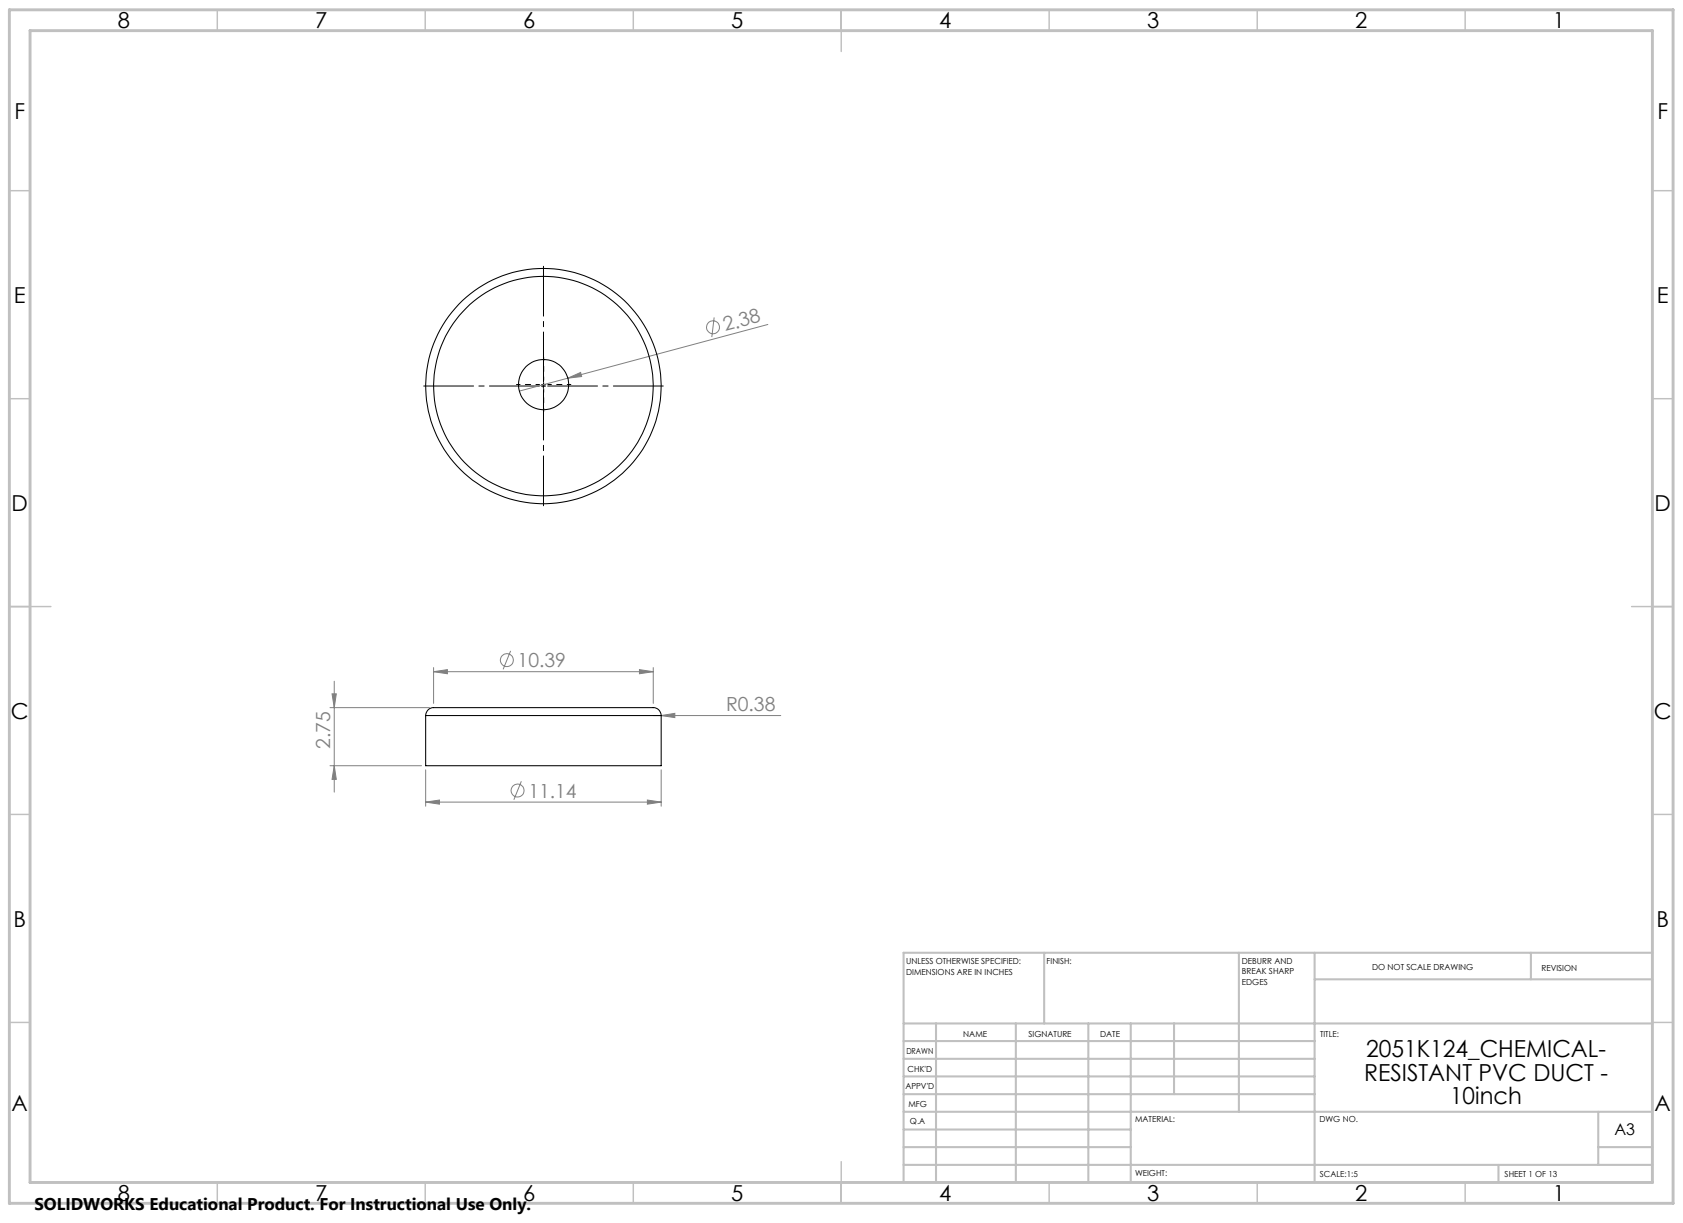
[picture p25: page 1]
FINISH:; DEBURR AND; BREAK SHARP; DO NOT SCALE DRAWING; REVISION; SCALE:1:5; SHEET 1 OF 13

UNLESS OTHERWISE SPECIFIED:
DIMENSIONS ARE IN INCHES

NAME | SIGNATURE | DATE | | | | TITLE: 2051K124_CHEMICAL-RESISTANT PVC DUCT -10inch

DRAWN
CHK'D
APPV'D
MFG
Q.A | | | | MATERIAL: | DWG NO. | A3

SOLIDWORKS Educational Product. For Instructional Use Only.

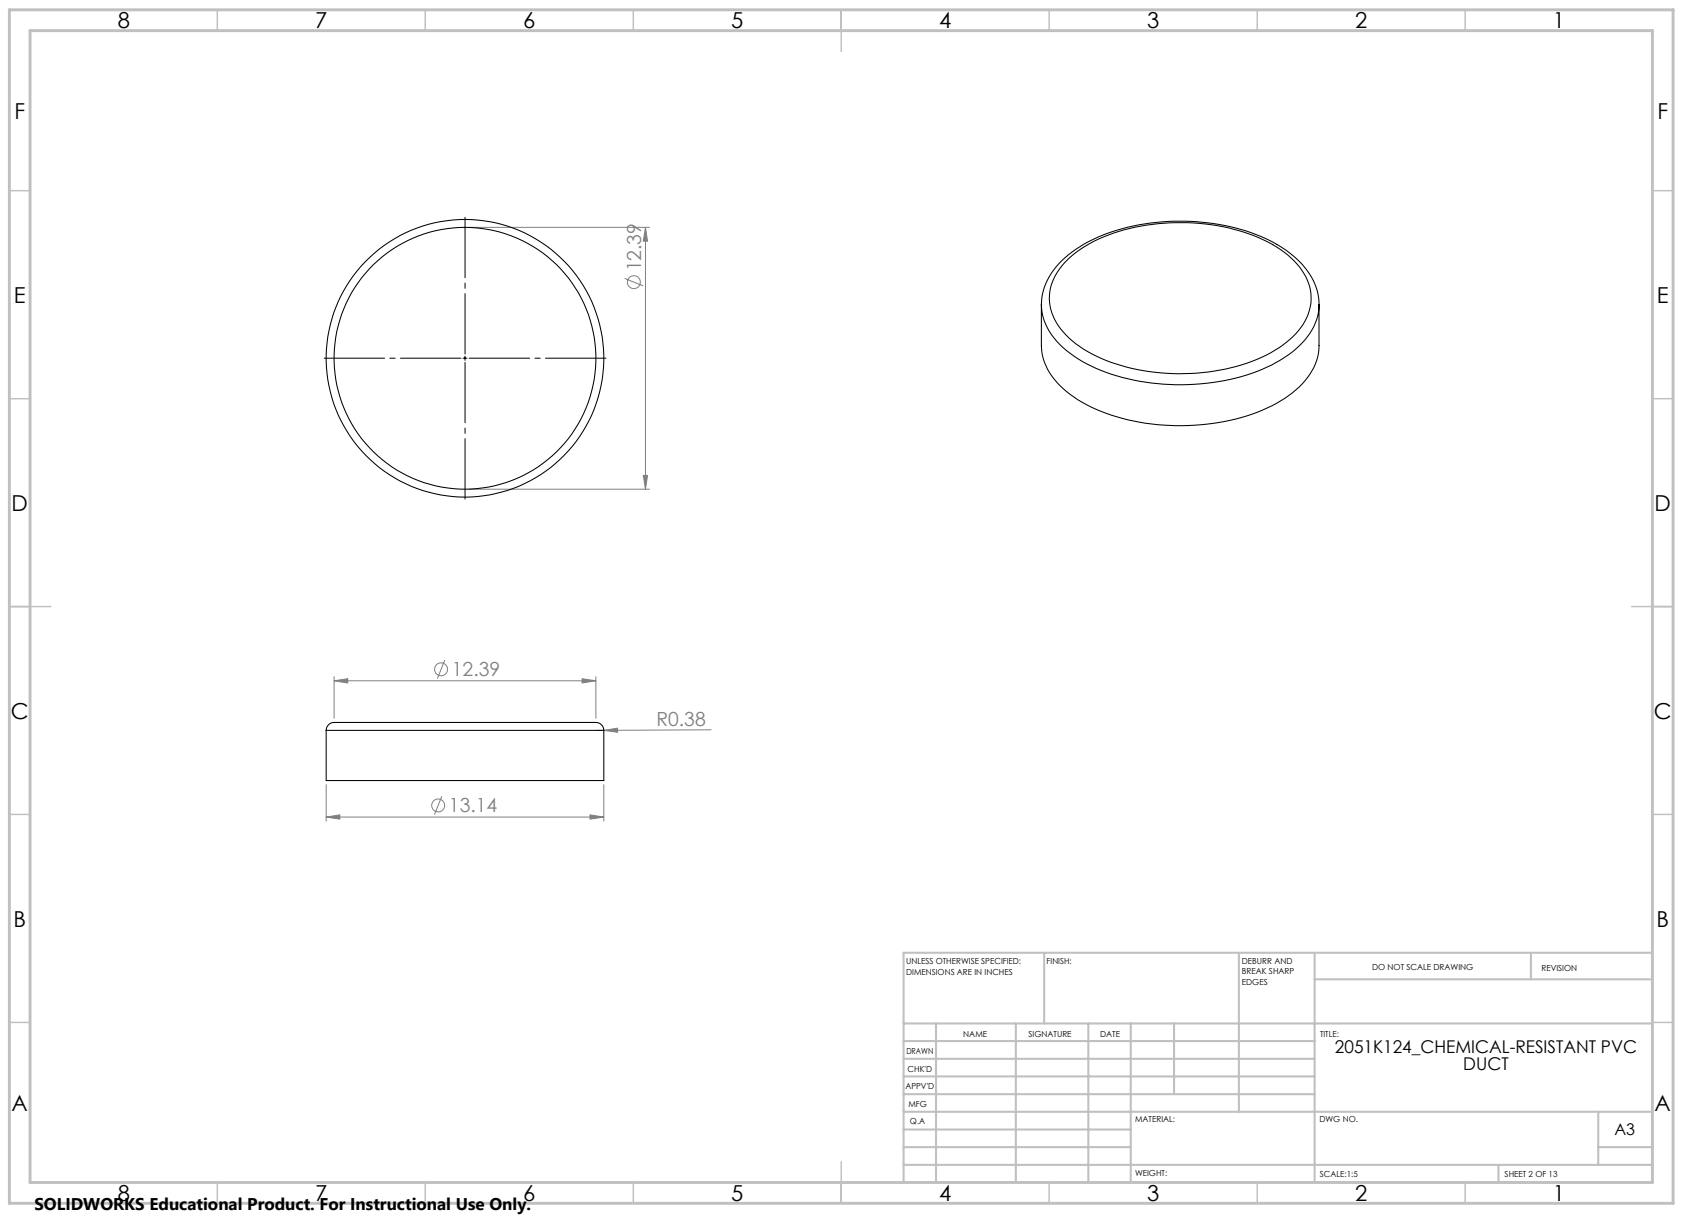
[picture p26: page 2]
FINISH:; DEBURR AND; BREAK SHARP; DO NOT SCALE DRAWING; REVISION; SCALE:1:5; SHEET 2 OF 13

UNLESS OTHERWISE SPECIFIED:
DIMENSIONS ARE IN INCHES

NAME | SIGNATURE | DATE | TITLE: 2051K124_CHEMICAL-RESISTANT PVC DUCT

DRAWN
CHK'D
APPV'D
MFG

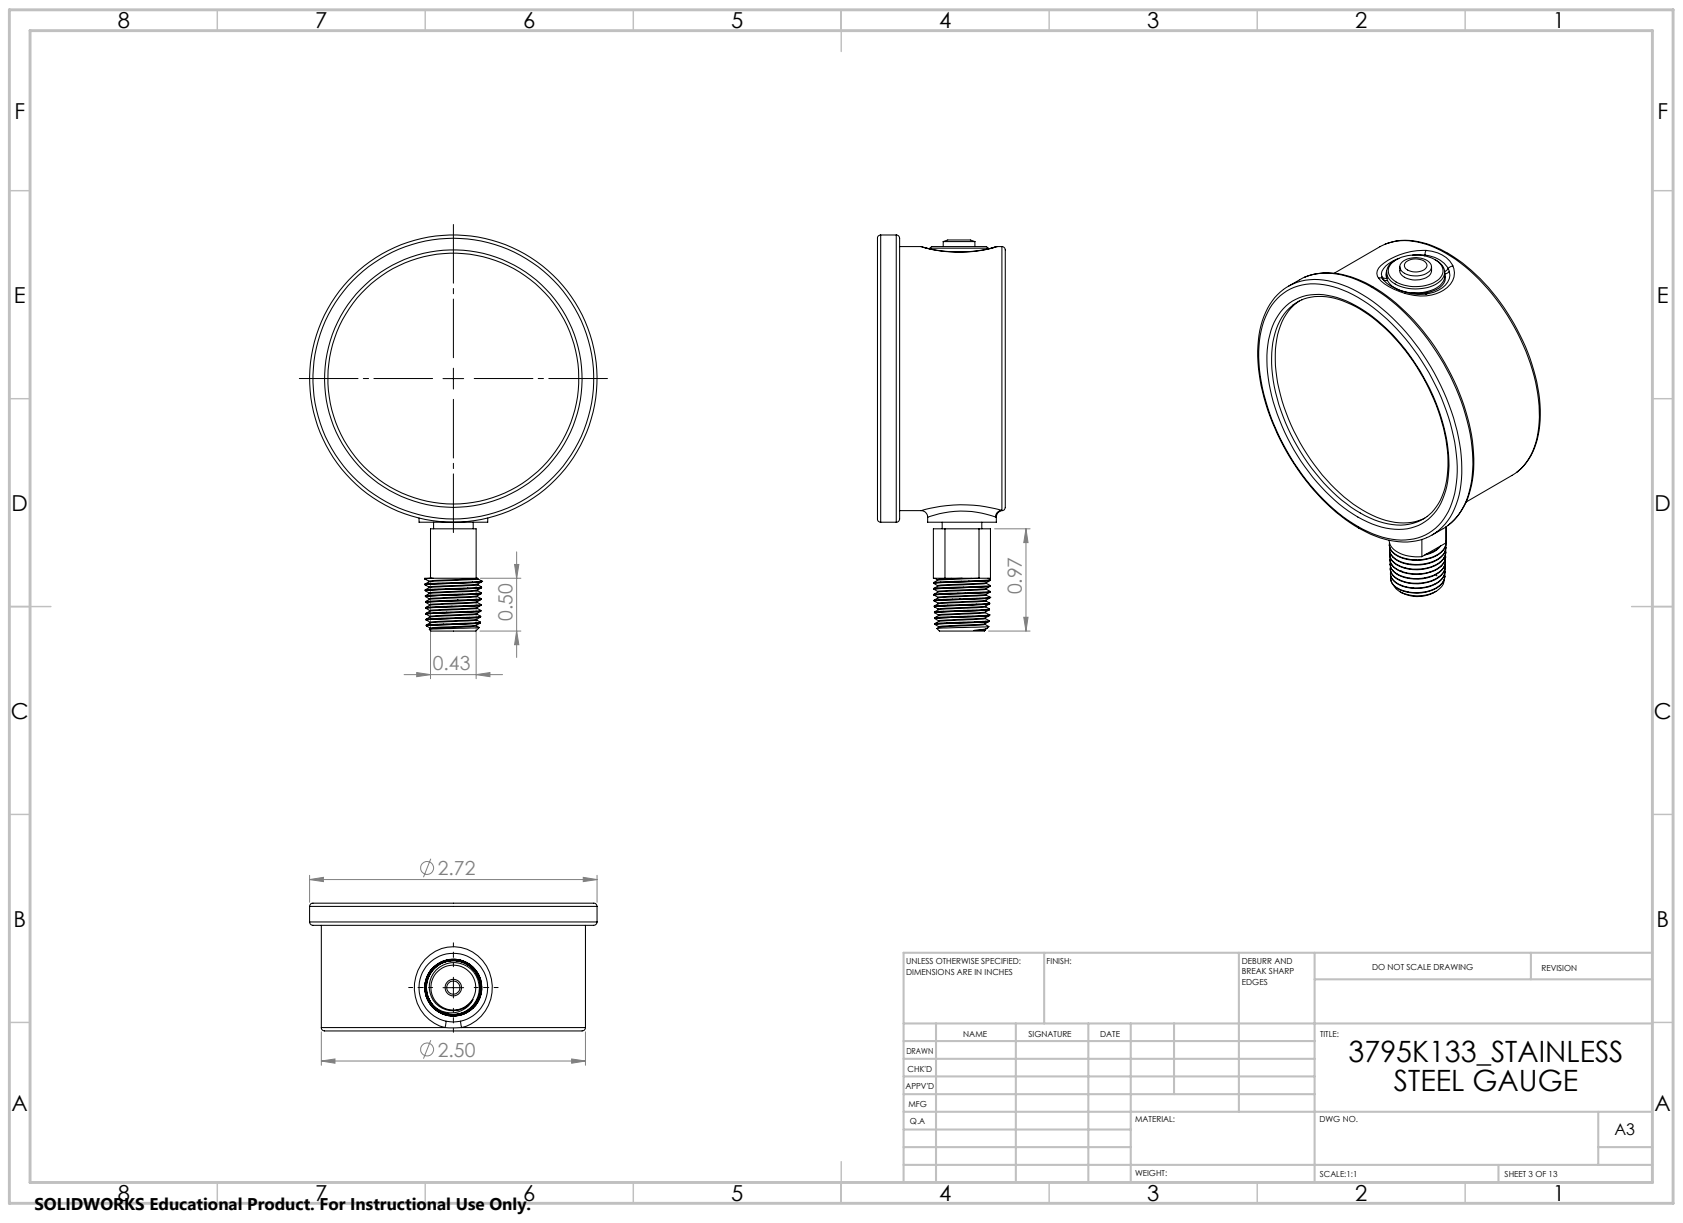
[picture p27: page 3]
FINISH:; DEBURR AND; BREAK SHARP; DO NOT SCALE DRAWING; REVISION; SCALE:1:1; SHEET 3 OF 13

UNLESS OTHERWISE SPECIFIED:
DIMENSIONS ARE IN INCHES

NAME | SIGNATURE | DATE | TITLE: 3795K133_STAINLESS STEEL GAUGE

DRAWN
CHK'D
APPV'D
MFG

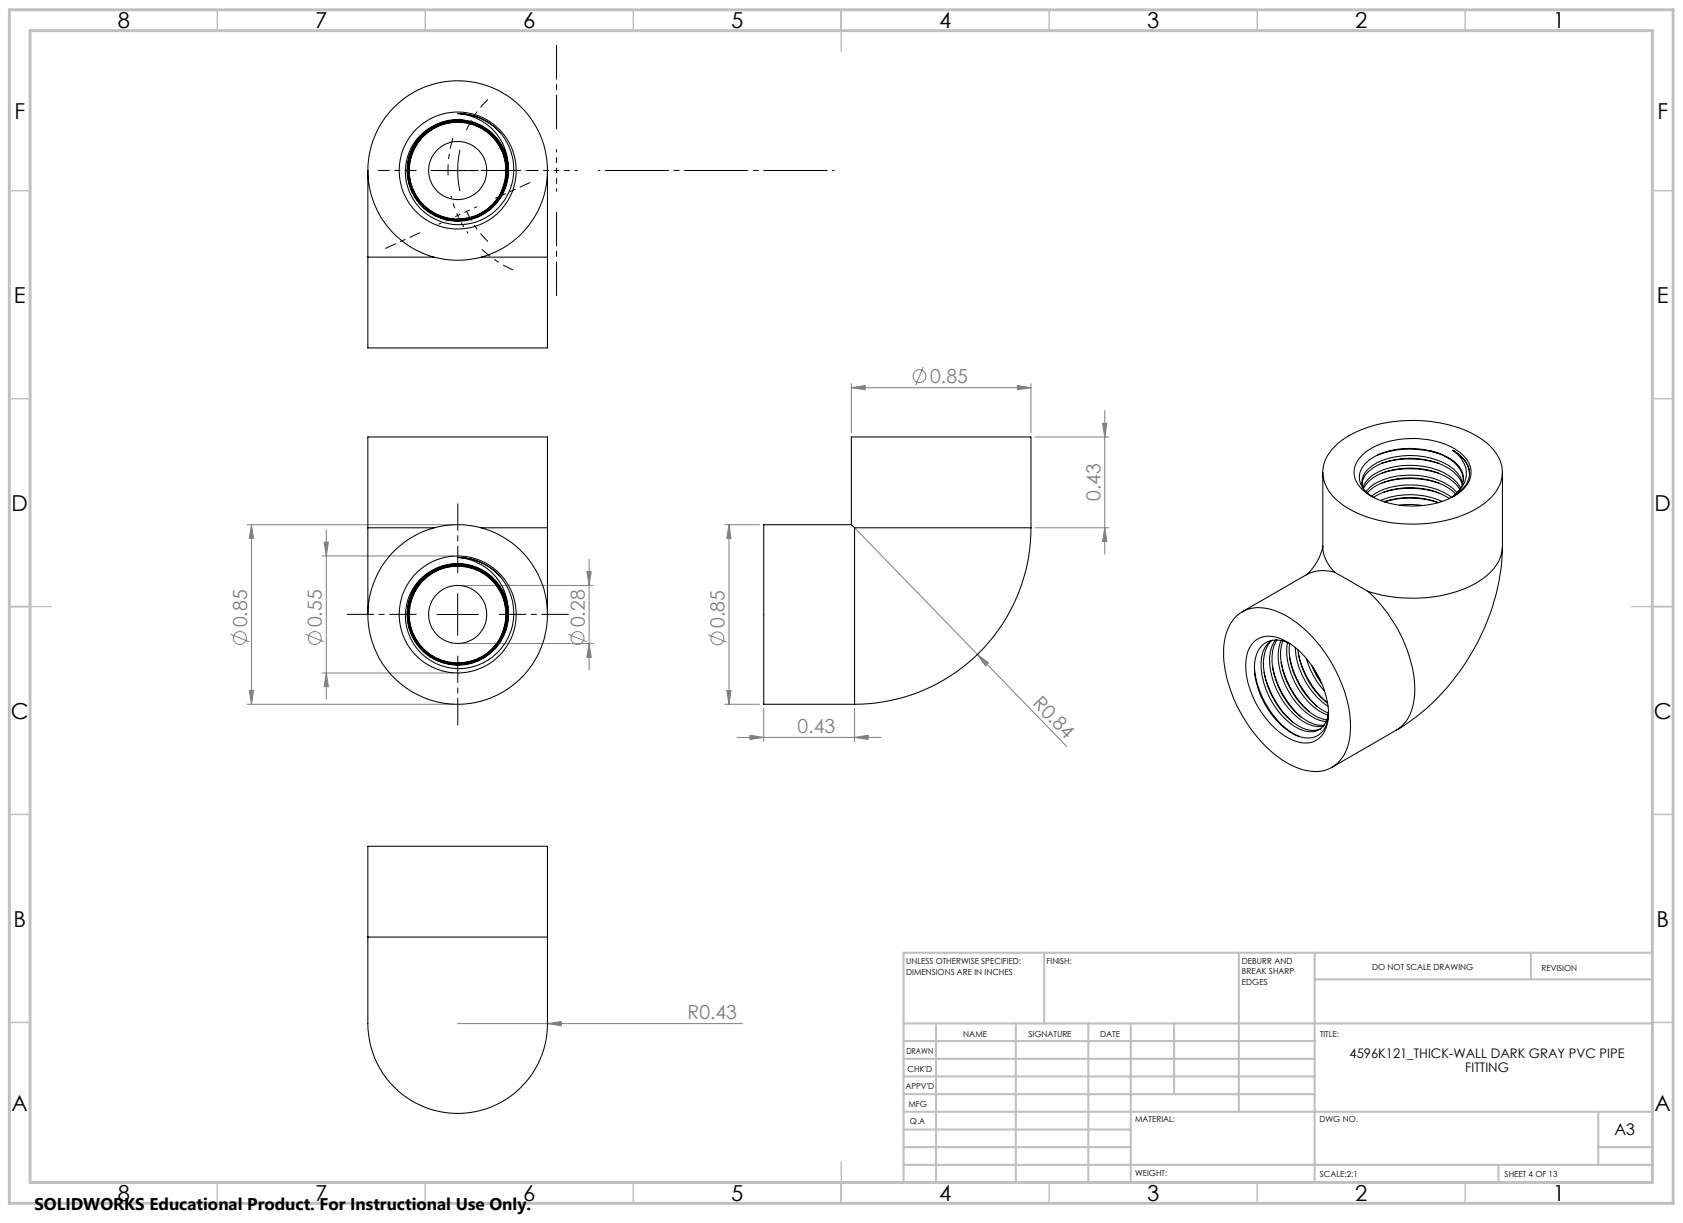
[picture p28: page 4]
FINISH:; DEBURR AND; BREAK SHARP; DO NOT SCALE DRAWING; REVISION; SCALE:2:1; SHEET 4 OF 13

UNLESS OTHERWISE SPECIFIED:
DIMENSIONS ARE IN INCHES

NAME | SIGNATURE | DATE | TITLE: 4596K121_THICK-WALL DARK GRAY PVC PIPE FITTING

DRAWN
CHK'D
APPV'D
MFG

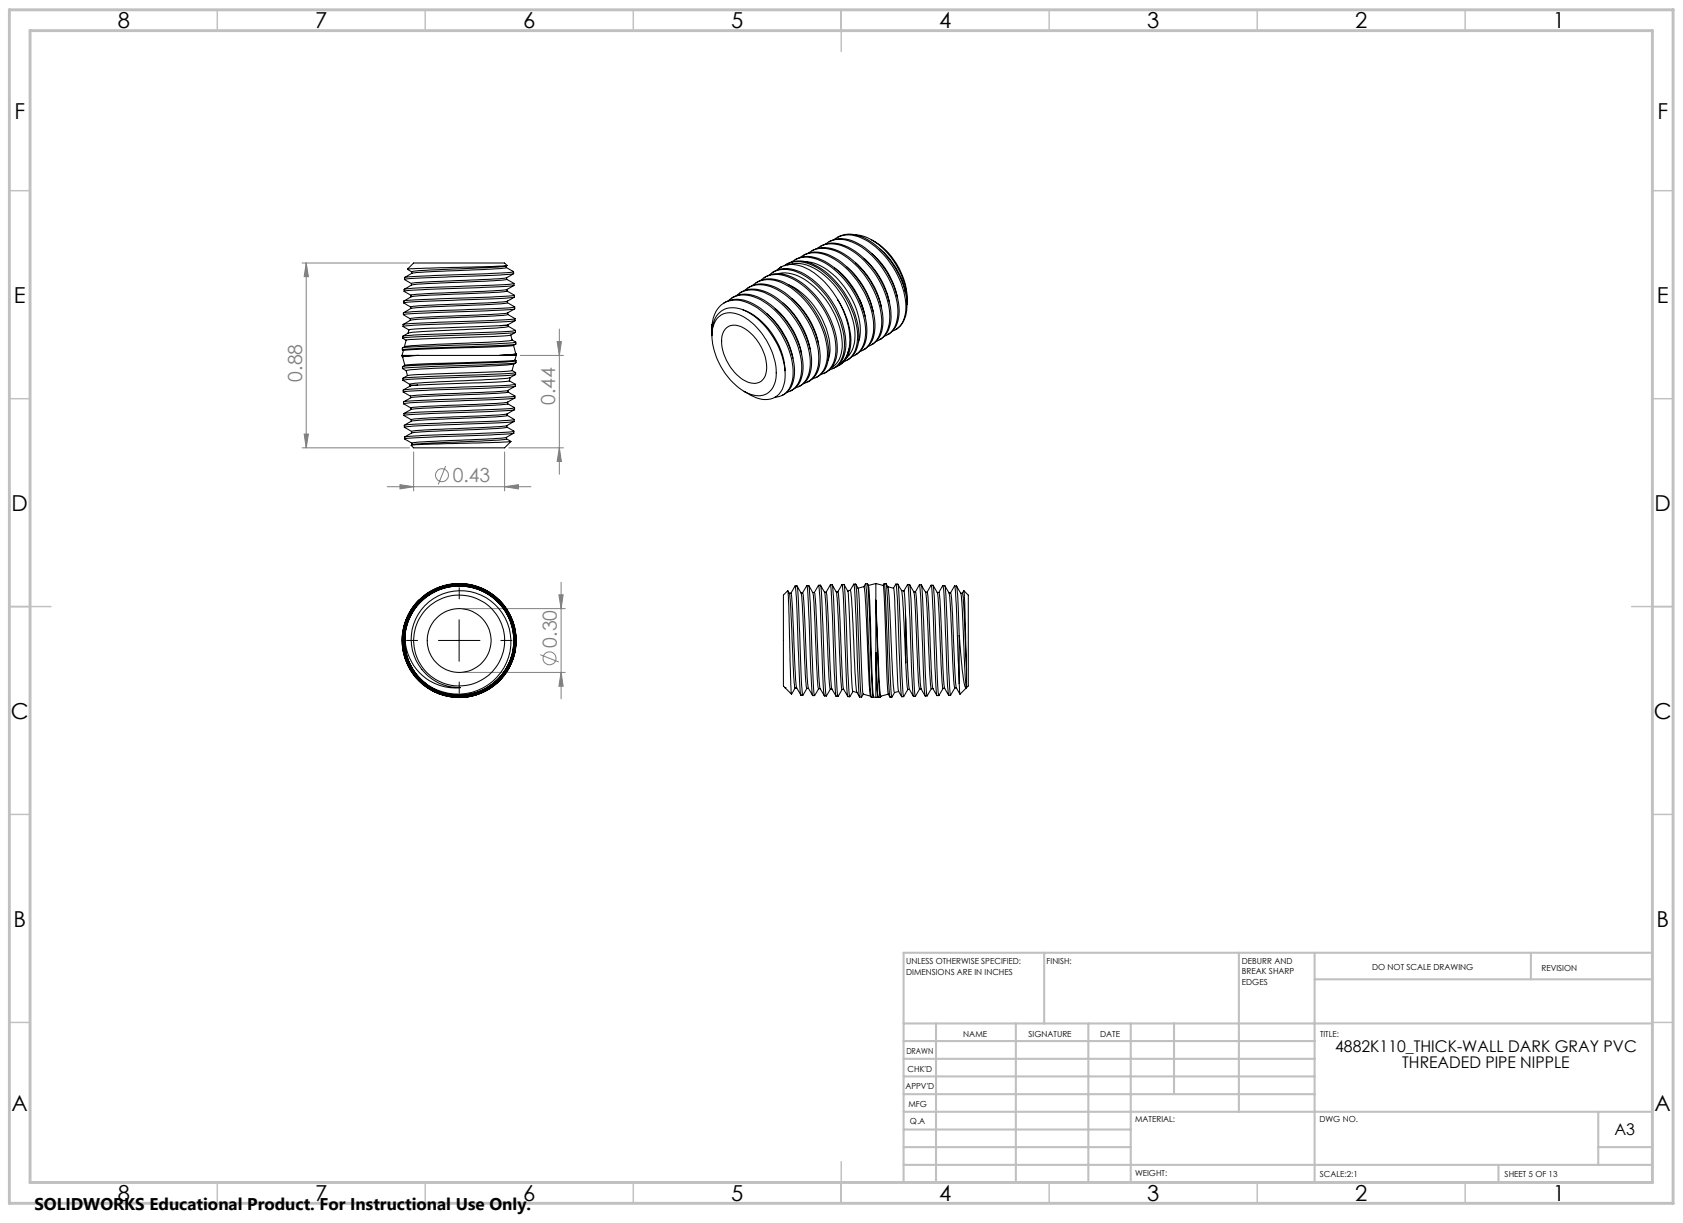
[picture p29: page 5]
FINISH:; DEBURR AND; BREAK SHARP; DO NOT SCALE DRAWING; REVISION

UNLESS OTHERWISE SPECIFIED:
DIMENSIONS ARE IN INCHES

NAME | SIGNATURE | DATE | TITLE: 4882K110_THICK-WALL DARK GRAY PVC THREADED PIPE NIPPLE

DRAWN
CHK'D
APPV'D
MFG

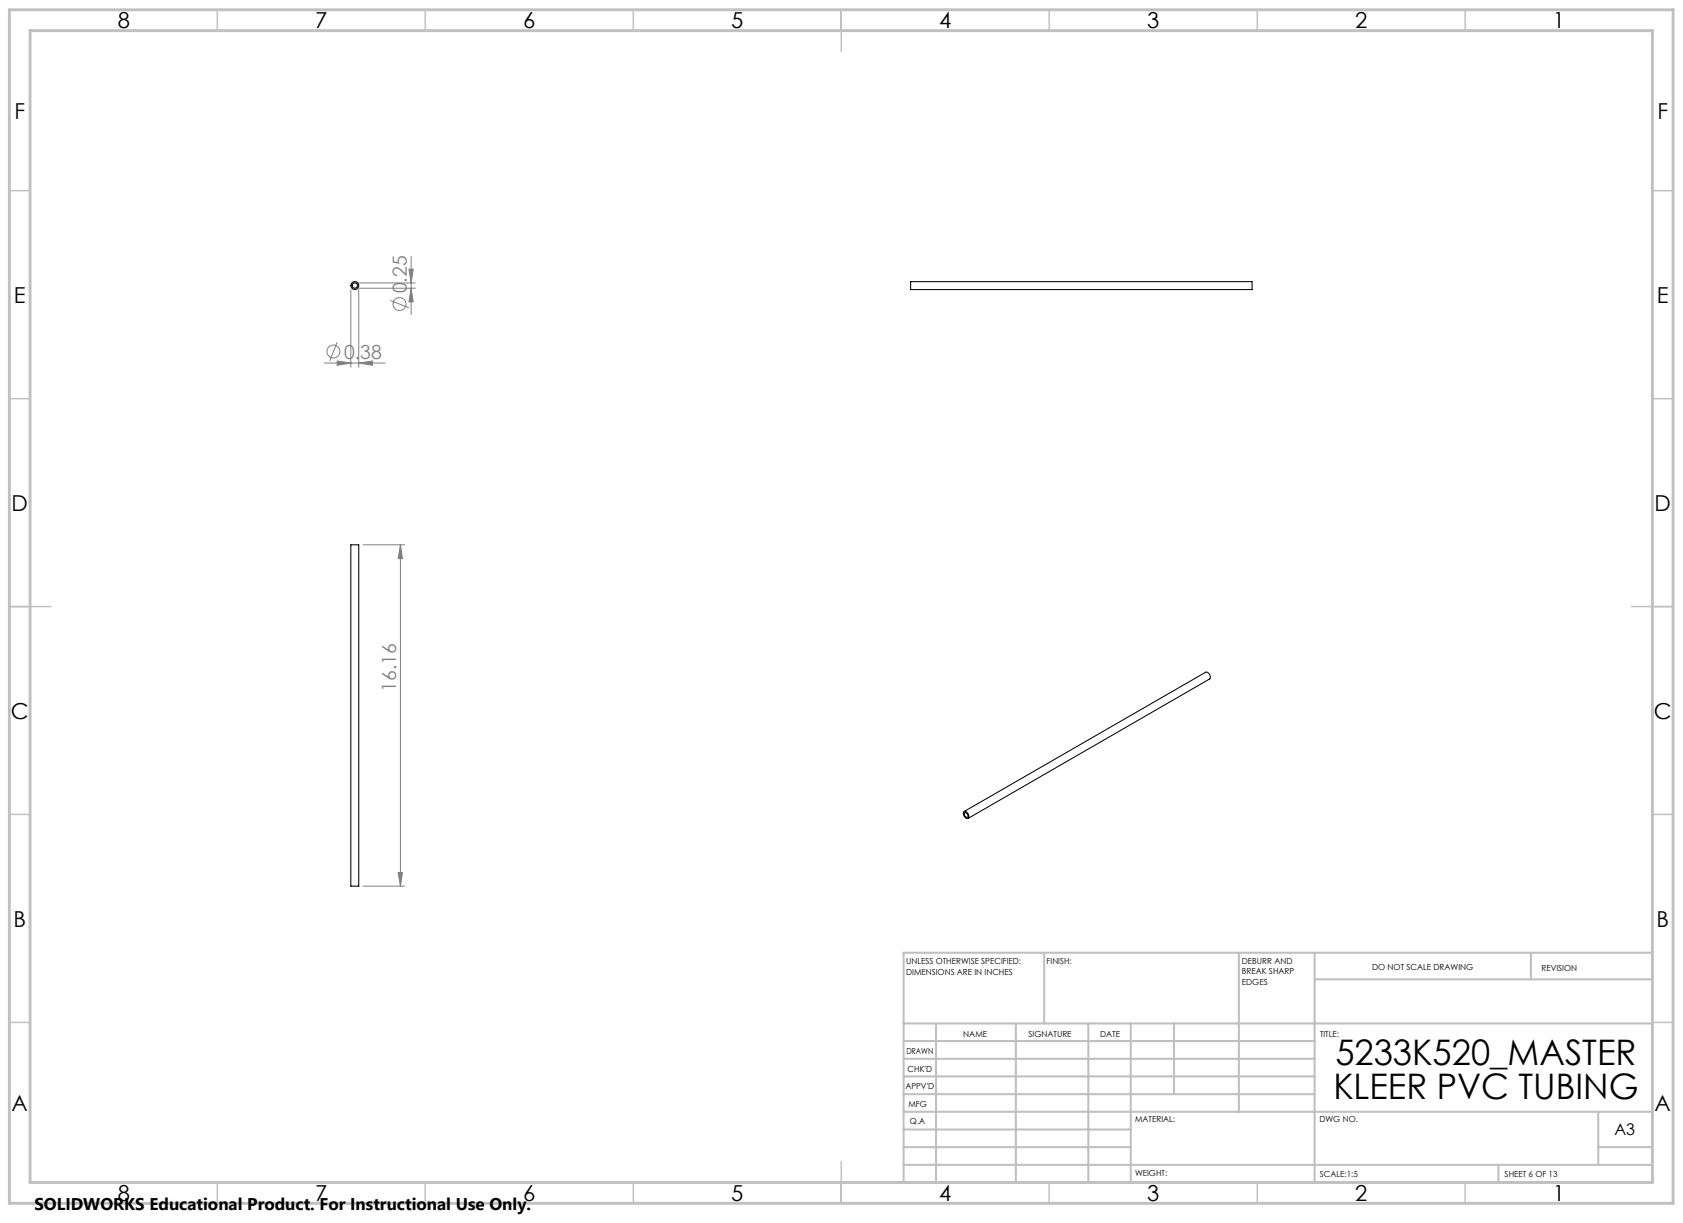
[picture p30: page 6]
FINISH:; DEBURR AND; BREAK SHARP; DO NOT SCALE DRAWING; REVISION; SCALE:1:5; SHEET 6 OF 13

UNLESS OTHERWISE SPECIFIED:
DIMENSIONS ARE IN INCHES

NAME | SIGNATURE | DATE | TITLE: 5233K520_MASTER KLEER PVC TUBING

DRAWN
CHK'D
APPV'D
MFG

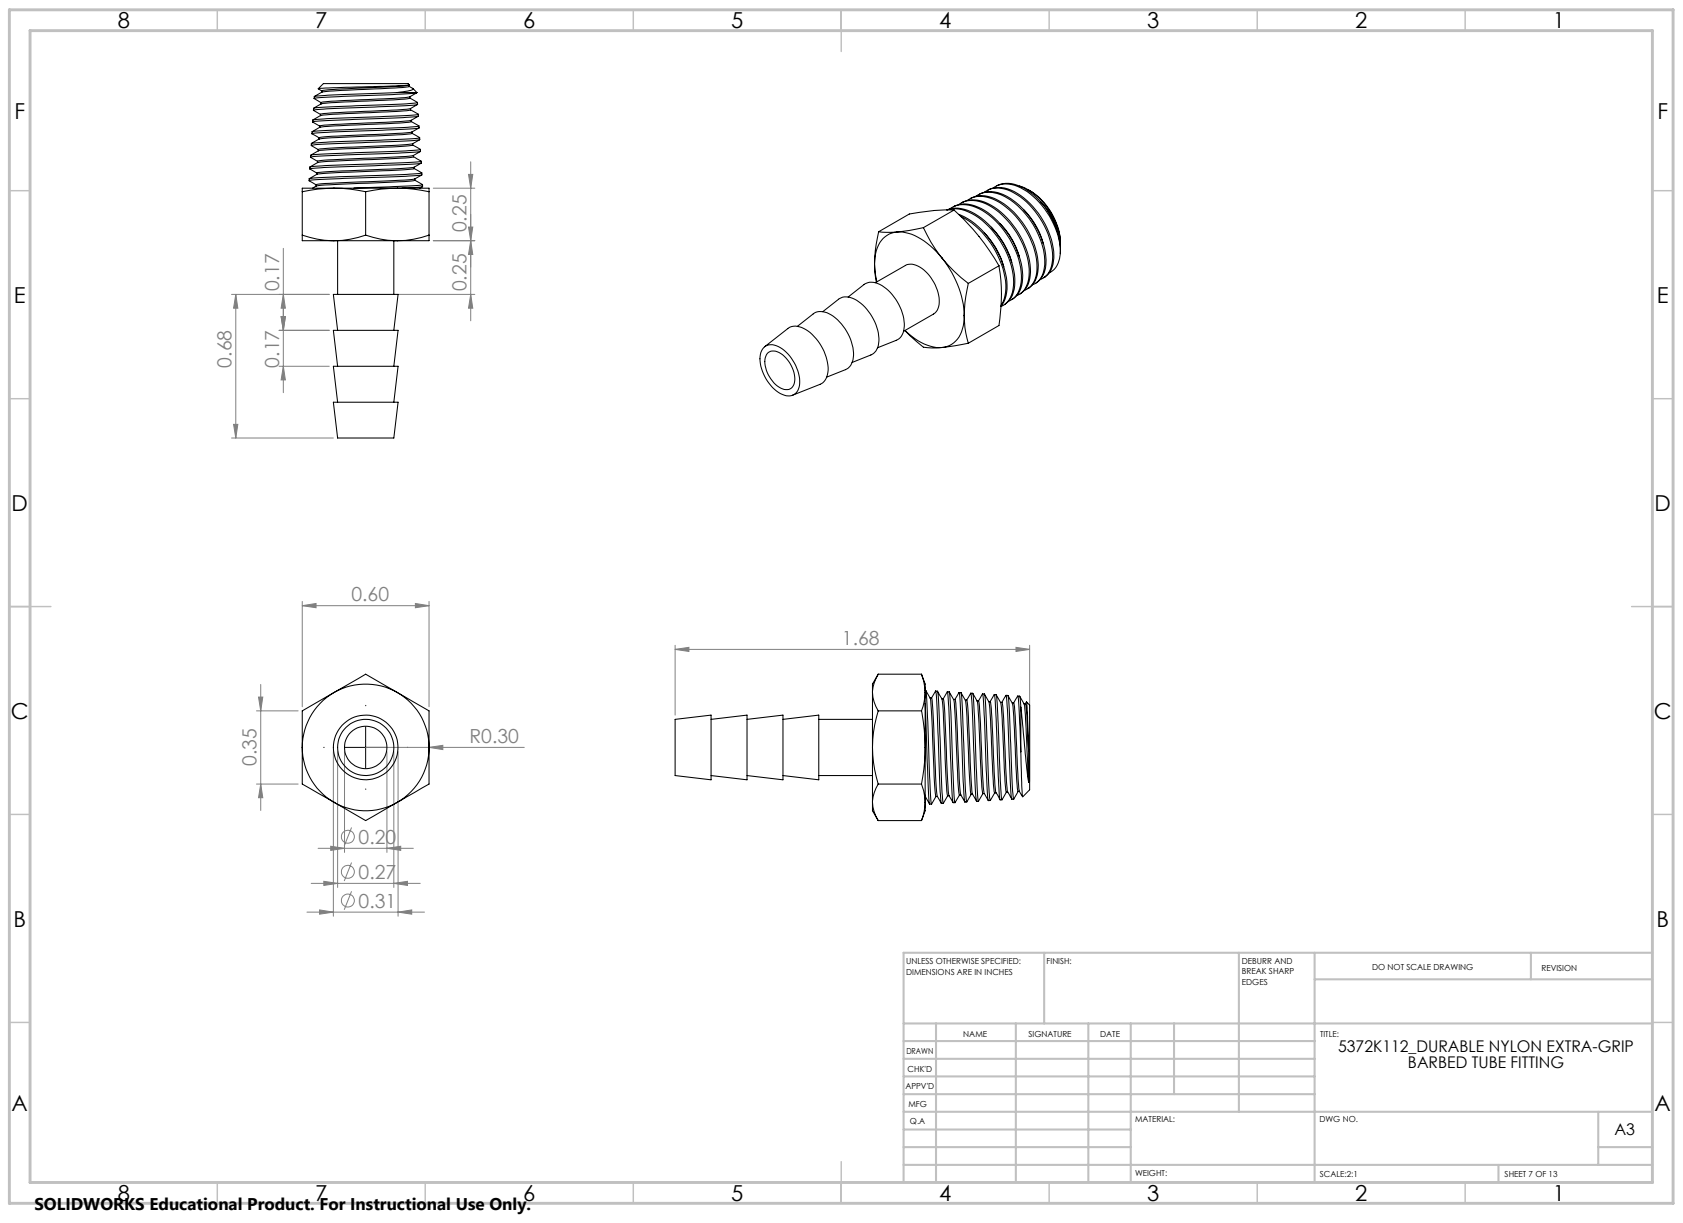
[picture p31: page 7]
FINISH:; DEBURR AND; BREAK SHARP; DO NOT SCALE DRAWING; REVISION

UNLESS OTHERWISE SPECIFIED:
DIMENSIONS ARE IN INCHES

NAME | SIGNATURE | DATE | TITLE: 5372K112_DURABLE NYLON EXTRA-GRIP BARBED TUBE FITTING

DRAWN
CHK'D
APPV'D
MFG

FINISH:; DEBURR AND; BREAK SHARP; DO NOT SCALE DRAWING; REVISION

UNLESS OTHERWISE SPECIFIED:
DIMENSIONS ARE IN INCHES

NAME | SIGNATURE | DATE | TITLE: 5779K638_PUSH-TO-CONNECT TUBE FITTING FOR AIR

DRAWN
CHK'D
APPV'D
MFG

FINISH:; DEBURR AND; BREAK SHARP; DO NOT SCALE DRAWING; REVISION

UNLESS OTHERWISE SPECIFIED:
DIMENSIONS ARE IN INCHES

NAME | SIGNATURE | DATE | TITLE: 9173K740_THK-WALL DK GRAY PVC THRD-ONE-END PIPE NIPPLE

DRAWN
CHK'D
APPV'D
MFG

FINISH:; DEBURR AND; BREAK SHARP; DO NOT SCALE DRAWING; REVISION; SCALE:1:10; SHEET 10 OF 13

UNLESS OTHERWISE SPECIFIED:
DIMENSIONS ARE IN INCHES

NAME | SIGNATURE | DATE | TITLE: PI-001 (12''PVC pipe bottom)

DRAWN
CHK'D
APPV'D
MFG

FINISH:; DEBURR AND; BREAK SHARP; DO NOT SCALE DRAWING; REVISION; SCALE:1:10; SHEET 11 OF 13

UNLESS OTHERWISE SPECIFIED:
DIMENSIONS ARE IN INCHES

NAME | SIGNATURE | DATE | TITLE: PI-002 (top 10'' PVC)

DRAWN
CHK'D
APPV'D
MFG

FINISH:; DEBURR AND; BREAK SHARP; DO NOT SCALE DRAWING; REVISION; SCALE:1:5; SHEET 12 OF 13

UNLESS OTHERWISE SPECIFIED:
DIMENSIONS ARE IN INCHES

NAME | SIGNATURE | DATE | TITLE: PI-003 (2'' Serrated PVC pipe)

DRAWN
CHK'D
APPV'D
MFG

FINISH:; DEBURR AND; BREAK SHARP; DO NOT SCALE DRAWING; REVISION

UNLESS OTHERWISE SPECIFIED:
DIMENSIONS ARE IN INCHES

NAME | SIGNATURE | DATE | TITLE: PI-004 (PVC pipe for fitting)

DRAWN
CHK'D
APPV'D
MFG

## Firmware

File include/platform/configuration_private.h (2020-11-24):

/*
 * configuration_private.h
 *
 * This file contains mappings of hardware pins/addresses
 * to specific devices used by the gVent system.
 *
 * Should map, for example, the pins controlling a valve
 * to a constant like INSP_VALVE_OPEN.
 *
 */
#ifndef INC_PLATFORM_CONFIGURATION_PRIVATE_H_
#define INC_PLATFORM_CONFIGURATION_PRIVATE_H_
#include "stm32f4xx_hal.h"

#define STATUS_LED_PORT     GPIOA
#define STATUS_LED_PIN      GPIO_PIN_5

/************************************************
 * VALVE CONTROL DEFINITIONS
 ************************************************/
// GPIO PA6 maps to Pin D12 on the Nucleo-64 board.
#define INSP_VALVE_PORT     GPIOA
#define INSP_VALVE_PIN      GPIO_PIN_6
// Pin PA7 maps to Pin D11 on the Nucleo-64 board.
#define EXP_VALVE_PORT      GPIOA
#define EXP_VALVE_PIN       GPIO_PIN_7
// GPIO PB6 maps to Pin D10 on the Nucleo-64 board.
#define TANK_VALVE_PORT     GPIOB
#define TANK_VALVE_PIN      GPIO_PIN_6

/************************************************
 * ALARM CONTROL DEFINITIONS
 ************************************************/

// GPIO PA9 maps to Pin D8 on the Nucleo-64 board.
#define ALARM_LED_PORT      GPIOA
#define ALARM_LED_PIN       GPIO_PIN_9

// GPIO PC7 maps to Pin D9 (PWM) on the Nucleo-64 board.

// Note that timer channels directly map to alternative
// functions of GPIO pins. TIM3.ch2 maps to PC7 on the 
// STM32F401RE microprocessor.
#define ALARM_BUZZ_PORT     GPIOC
#define ALARM_BUZZ_PIN      GPIO_PIN_7
#define ALARM_BUZZ_TIM      TIM3
#define ALARM_BUZZ_CHL      TIM_CHANNEL_2
#define ALARM_BUZZ_AF2      GPIO_AF2_TIM3

// frequency of the alarm buzzer in Hz.
#define ALARM_BUZZ_FREQ     1000

// globally available handle for the alarm timer.
TIM_HandleTypeDef alarm_timer;

/************************************************
 * I2C CONTROL DEFINITIONS
 ************************************************/

// GPIO PB9 maps to Pin D14 (I2C1_SDA) on the Nucleo-64 board.
#define I2C_PORT            GPIOB
#define I2C_SDA_PIN         GPIO_PIN_9

// GPIO PB8 maps to Pin D15 (I2C1_SCL) on the Nucleo-64 board.
#define I2C_PORT            GPIOB
#define I2C_SCL_PIN         GPIO_PIN_8

// globally available handle for the i2c peripheral.
I2C_HandleTypeDef i2c1_bus;

// firmware-set i2c addresses for the FS6122 sensors
#define INSPIRATORY_ADDR    0x1D << 1       // sensor 1
#define EXPIRATORY_ADDR     0x02 << 1       // sensor 2

#endif /* INC_PLATFORM_CONFIGURATION_PRIVATE_H_ */

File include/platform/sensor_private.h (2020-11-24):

/*
 * sensor_private.h
 *
 * private to the platform
 */

#ifndef INC_PLATFORM_MEASURED_INPUTS_H_
#define INC_PLATFORM_MEASURED_INPUTS_H_

/*=========================================================================
    I2C ADDRESS/BITS
    -----------------------------------------------------------------------*/
#define FS6122_DEFAULT_ADDRESS                 (0x1D)
/*=========================================================================*/

/////////////////////////////////////
// Hex Byte Commands for fs6122
// WRITE COMMANDS
#define FS6122_WRITE_ADDRESS            0x05 // write the i2c address, Bit7 ~ Bit1 can be set in hex (0x08 means address of 4)
#define FS6122_WRITE_FILTERDEPTH        0x0B // write the filter depth Int8, 0-254
#define FS6122_CAL_FLOWRATE_OFFSET      0x1C // calibration the offset of the flow rate, 1 byte, any value, ensure NO flow in the pipe
#define FS6122_CAL_PRESSURE_OFFSET      0x24 // calibration of offset of pressure, 1 byte, any value, ensure NO flow in the pipe

// READ COMMANDS
#define FS6122_READ_SENSOR_SN           0x82 // Serial Number of the sensor in ASCII
#define FS6122_READ_FLOWRATE            0x83 // Int32/1000 SLPM
#define FS6122_READ_FLOWRATE_PRESSURE   0x84 // Int32/1000 SLPM, int32/1000 cmH20

#define FS6122_READ_ADDRESS             0x85 // Bit7 ~ Bit1
#define FS6122_READ_FILTERDEPTH         0x8B // Int8, 0~254
#define FS6122_READ_PRESSURE            0xA3 // Int32/1000 cmH20
#define FS6122_READ_TEMPERATURE         0x82  // Int16/100 deg celcius
#define FS6122_READ_HUMIDITY            0x83  // Int16/100 %RH


/*=========================================================================
    SENSOR PHYSICAL BOUNDS
    -----------------------------------------------------------------------
	Defines the upper and lower bounds for the FS6122 pressure and 
	flow sensor, based on the specification sheet available at 
	https://www.servoflo.com/download-archive/data-sheets/254-mass-flow-vacuum-sensors/1220-fs6122-datasheet
	or at 
	https://github.com/patchworquill/fs6122/blob/master/fs6122_datasheet.pdf

	### FS6122
	| Pin | Color | Definition | 
	| :-- | :-- | :-- |
	| 1 | White | P_out, Pressure analog sensor output
	| 2 | Green | F_out, Flow analog sensor output 
	| 3 | Black | GND, Ground
	| 4 | Red | VCC, Power supply
	| 5 | Yellow | SCL 
	| 6 | Blue | SDA 
	
=========================================================================*/

/*
* The worstcase tolerable latency (in ms) for which the sensed inputs are valid
*/
#define PRESSURE_MAXIMUM_LATENCY 1000
#define FLOW_MAXIMUM_LATENCY 1000

/*
* The minimum latency (in ms) for the sensed inputs under which read are not necessary
*/
#define PRESSURE_MINIMUM_LATENCY 1
#define FLOW_MINIMUM_LATENCY 1

/*
 * The lower and upper bounds of validity for the sensed inputs
 * pressure bounds are given in cmH2O
 * flow  bounds are given in SLPM
 */
#define PRESSURE_LOWER_BOUND -5000
#define PRESSURE_UPPER_BOUND 40000
#define FLOW_LOWER_BOUND -250000
#define FLOW_UPPER_BOUND 250000

/*
 * The maximum change rate
 * pressure change rate given in cmH2O per second
 * flow change rate given in SLPM
 */
#define PRESSURE_MAX_CHANGE_RATE 10
#define FLOW_MAX_CHANGE_RATE 10


// Internal I2C Error codes
typedef enum {
    I2C_OK = 0x00,   // operation complete without error.
    TRANSMIT_ERROR = 0x02,   // operation failed.
    RECEIVE_ERROR = 0x04,
    I2C_ERROR = 0x10
} sensor_status_t;

/* 
 * Private i2c read function for the FS6122 sensor
 * first byte is the i2c sensor address
 * second byte is the flow/pressure/temp/RH select byte
 */

sensor_status_t read_FS6122_sensor(uint8_t, uint8_t, uint32_t *);

/**
 * Definition of the measured inputs data structure
 */
typedef struct MeasurementsStatus {
	/**
	 * The last read value for the inspiratory pressure
	 */
	int inspiratory_pressure;
	/*
	 * the time at which the above inspiratory pressure was read
	 */
	int last_inspiratory_pressure_read_time;

	/*
	 * The last read value for the expiratory pressure
	 */
	int expiratory_pressure;
	/*
	* the time at which the above expiratory pressure was read
	*/
	int last_expiratory_pressure_read_time;

	/*
	* The last read value for the inspiratory flow
	*/
	int inspiratory_flow;
	/*
	* the time at which the above inspiratory flow was read
	*/
	int last_inspiratory_flow_read_time;

	/*
	* The last read value for the expiratory flow
	*/
	int expiratory_flow;
	/*
	 * the time at which the above expiratory flow was read
	*/
	int last_expiratory_flow_read_time;
} measurements_status_t;


#endif /* INC_PLATFORM_MEASURED_INPUTS_H_ */

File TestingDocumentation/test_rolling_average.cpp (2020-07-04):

#include <stdio.h>
#include <stdlib.h>
#include <time.h>
#include <unistd.h>

#define AVG_PRESSURE_ARR_SECONDS 10
#define AVG_PRESSURE_PER_SECOND 1
#define AVG_PRESSURE_ARR_LENGTH AVG_PRESSURE_ARR_SECONDS*AVG_PRESSURE_PER_SECOND

#define AVG_FR_ARR_SECONDS 10
#define AVG_FR_PER_SECOND 1
#define AVG_FR_ARR_LENGTH AVG_FR_ARR_SECONDS*AVG_FR_PER_SECOND

void assert(float val1, float val2){
  static unsigned int success = 0;
  static unsigned int fail = 0;
  float diff = val2 - val1;
  diff = diff < 0? diff : -1*diff;
  if(diff < 0.00001){
    success++;
  }
  else{
    fail++;
    printf("%f doesn't equal %f\n", val1, val2);
  }
  printf("%u successes, %u failures\n", success, fail);
}

unsigned int millis(){
  return int(1000*clock()/(1.0*CLOCKS_PER_SEC));
}

void wait(unsigned wait_time){
  unsigned int start = millis();
  while(millis()-start < wait_time){}
}

float update_rolling_avg(float new_val, float arr[], unsigned int* arr_index,
  unsigned int arr_length, bool* arr_filled, float* avg_sum, unsigned int* avg_count,
  unsigned int period, unsigned long* last_compute){
  if(!(*last_compute)){ // adjust for wait before first value
    *last_compute = millis();
  }
  *avg_sum += new_val;
  (*avg_count)++;

  // add new entry to array every second
  if (millis() - *last_compute >= period){
    *last_compute += period;
    arr[*arr_index] = *avg_sum/(*avg_count);

    // the following block of code backfills the array to compensate for very long missed periods
    while(millis() - *last_compute >= period){
      *arr_index = (*arr_index + 1) % arr_length;
      arr[*arr_index] = *avg_sum/(*avg_count);
      *last_compute += period;
    }

    *avg_sum = 0;
    *avg_count = 0;
    (*arr_index)++;

    if (*arr_index == arr_length){ // restart array and raise flag tat array has been populated
      *arr_filled = true;
      *arr_index = 0;
    }

    // calculate average of last 60s (or since start of measurements if it's been less than 60s)
    float total_avg; // the average of the values in the array
    if(*arr_filled){
      float total_sum = 0;
      for(int i = 0; i < arr_length; i++){
        total_sum += arr[i];
      }
      total_avg = total_sum/arr_length;
    }
    else{
      float total_sum = 0;
      for(int i = 0; i < *arr_index; i++){
        total_sum += arr[i];
      }
      total_avg = total_sum/(*arr_index);
    }
    return total_avg;
  }
  float ret_val;
  if(!(*arr_filled)&&(*arr_index==0)){
    return (*avg_sum/float(*avg_count));
  }
  return -1.0;
}

float update_rolling_avg_pressure(float new_val){
  static float avg_pressure_arr[AVG_PRESSURE_ARR_LENGTH]; // circular array containing pressure values
  static unsigned int arr_index = 0; // the index of the array head
  static bool arr_filled = false; // whether or not the array has been fully populated

  static float avg_sum = 0;
  static unsigned int avg_count = 0;
  static float avg_pressure = 0;
  static unsigned long* last_compute = (unsigned long*) calloc(0, sizeof(unsigned long));

  float ret_val = update_rolling_avg(new_val, avg_pressure_arr, &arr_index, AVG_PRESSURE_ARR_LENGTH, &arr_filled, &avg_sum, &avg_count, AVG_PRESSURE_PER_SECOND*1000, last_compute);
  if (ret_val > 0.0){
    avg_pressure = ret_val;
  }
  return avg_pressure;
}

float update_rolling_avg_flowrate(float new_val){
  static float avg_fr_arr[AVG_FR_ARR_LENGTH]; // circular array containing flow rate values
  static unsigned int arr_index = 0; // the index of the array head
  static bool arr_filled = false; // whether or not the array has been fully populated

  static float avg_sum = 0;
  static unsigned int avg_count = 0;
  static float avg_fr = 0;
  static unsigned long* last_compute = (unsigned long*) calloc(0, sizeof(unsigned long));

  float ret_val = update_rolling_avg(new_val, avg_fr_arr, &arr_index, AVG_FR_ARR_LENGTH, &arr_filled, &avg_sum, &avg_count, AVG_FR_PER_SECOND*1000, last_compute);
  if (ret_val > 0.0){
    avg_fr = ret_val;
  }
  return avg_fr;
}

int main(){
  float avg_pressure;
  avg_pressure = update_rolling_avg_pressure(1.0);
  assert(avg_pressure, 1.0);
  avg_pressure = update_rolling_avg_pressure(2.5);
  assert(avg_pressure, 1.75);
  wait(1000);
  avg_pressure = update_rolling_avg_pressure(2.5); // 2/1
  assert(avg_pressure, 2.0);
  wait(1000);
  avg_pressure = update_rolling_avg_pressure(3); // 5/2
  assert(avg_pressure, 2.5);
  wait(2000);
  avg_pressure = update_rolling_avg_pressure(3.5); // 12/4
  assert(avg_pressure, 3.0);
  wait(500);
  avg_pressure = update_rolling_avg_pressure(6);
  assert(avg_pressure, 3.0);
  wait(500);
  avg_pressure = update_rolling_avg_pressure(4); // 17/5
  assert(avg_pressure, 17.0/5);
  wait(500);
  avg_pressure = update_rolling_avg_pressure(0.5);
  assert(avg_pressure, 17.0/5);
  wait(600);
  avg_pressure = update_rolling_avg_pressure(1.5); // 18/6
  assert(avg_pressure, 3.0);
  wait(900);
  avg_pressure = update_rolling_avg_pressure(6.5); // 24.5/7
  assert(avg_pressure, 3.5);
  wait(1000);
  avg_pressure = update_rolling_avg_pressure(3.5); // 28/8
  assert(avg_pressure, 3.5);
  wait(1000);
  avg_pressure = update_rolling_avg_pressure(3.5); // 31.5/9
  assert(avg_pressure, 3.5);
  wait(1000);
  avg_pressure = update_rolling_avg_pressure(3.5); // 35/10
  assert(avg_pressure, 3.5);
  wait(1000);
  avg_pressure = update_rolling_avg_pressure(3.5); // 36.5/10
  assert(avg_pressure, 3.65);
  wait(1000);
  avg_pressure = update_rolling_avg_pressure(1.5); // 35/10
  assert(avg_pressure, 3.5);
  wait(1000);
  avg_pressure = update_rolling_avg_pressure(4.0); // 35.5/10
  assert(avg_pressure, 3.55);
  wait(9000);
  avg_pressure = update_rolling_avg_pressure(4.1); // 40.9/10
  assert(avg_pressure, 4.09);

  float avg_fr;
  avg_fr = update_rolling_avg_flowrate(1.0);
  assert(avg_fr, 1.0);
  avg_fr = update_rolling_avg_flowrate(2.5);
  assert(avg_fr, 1.75);
  wait(1000);
  avg_fr = update_rolling_avg_flowrate(2.5); // 2/1
  assert(avg_fr, 2.0);
  wait(1000);
  avg_fr = update_rolling_avg_flowrate(3); // 5/2
  assert(avg_fr, 2.5);
  wait(2000);
  avg_fr = update_rolling_avg_flowrate(3.5); // 12/4
  assert(avg_fr, 3.0);
  wait(500);
  avg_fr = update_rolling_avg_flowrate(6);
  assert(avg_fr, 3.0);
  wait(500);
  avg_fr = update_rolling_avg_flowrate(4); // 17/5
  assert(avg_fr, 17.0/5);
  wait(500);
  avg_fr = update_rolling_avg_flowrate(0.5);
  assert(avg_fr, 17.0/5);
  wait(600);
  avg_fr = update_rolling_avg_flowrate(1.5); // 18/6
  assert(avg_fr, 3.0);
  wait(900);
  avg_fr = update_rolling_avg_flowrate(6.5); // 24.5/7
  assert(avg_fr, 3.5);
  wait(1000);
  avg_fr = update_rolling_avg_flowrate(3.5); // 28/8
  assert(avg_fr, 3.5);
  wait(1000);
  avg_fr = update_rolling_avg_flowrate(3.5); // 31.5/9
  assert(avg_fr, 3.5);
  wait(1000);
  avg_fr = update_rolling_avg_flowrate(3.5); // 35/10
  assert(avg_fr, 3.5);
  wait(1000);
  avg_fr = update_rolling_avg_flowrate(3.5); // 36.5/10
  assert(avg_fr, 3.65);
  wait(1000);
  avg_fr = update_rolling_avg_flowrate(1.5); // 35/10
  assert(avg_fr, 3.5);
  wait(1000);
  avg_fr = update_rolling_avg_flowrate(4.0); // 35.5/10
  assert(avg_fr, 3.55);
  wait(9000);
  avg_fr = update_rolling_avg_flowrate(4.1); // 40.9/10
  assert(avg_fr, 4.09);

  printf("test\n");
}

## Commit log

2020-04-01 Changed startButton to pin 7 since nano uses D4, D5 for i2c bus. Added comments
2020-04-08 Create Images
    Delete Images
    Add files via upload
    Update README.md
    Update README.md
    Update README.md
    Update README.md
    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
    [2051K124_CHEMICAL-RESISTANT PVC DUCT - 10inch.SLDPRT, 2051K124_CHEMICAL-RESISTANT PVC DUCT.SLDPRT, 3795K133_STAINLESS STEEL GAUGE.SLDPRT, 4596K121_THICK-WALL D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]
2020-04-08 Added Alarm 1: High/low peak pressure, and soundAlarm() function #6
2020-04-19 Added live update text and improved sensor simulator
2020-05-06 Working 2-sensor, 2-valve
2020-05-27 Codelife files added
    [2051K124_CHEMICAL-RESISTANT PVC DUCT - 10inch.SLDPRT, 2051K124_CHEMICAL-RESISTANT PVC DUCT.SLDPRT, 3795K133_STAINLESS STEEL GAUGE.SLDPRT, 4596K121_THICK-WALL D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]
2020-05-31 Added sensors.ino to interface w/ sensors
2020-05-31 added I2C devices comment in Vcontrol.ino
2020-06-22 Added gVent HAZOP file v1.0
    [gVent HAZOP.xlsx]
2020-10-07 New master branch, cleaned to begin software process controlled development of the platform and software application fo gVent towards v1.0 release. Assembly Instructions + CAD drawings moved to Hardw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
    [2051K124_CHEMICAL-RESISTANT PVC DUCT - 10inch.SLDPRT, 2051K124_CHEMICAL-RESISTANT PVC DUCT.SLDPRT, 3795K133_STAINLESS STEEL GAUGE.SLDPRT, 4596K121_THICK-WALL D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]
2020-10-17 Added platformio.ini with config for STM32F401re
2020-10-21 Add Unit testing Framework and rename documentation folder
    [2051K124_CHEMICAL-RESISTANT PVC DUCT - 10inch.SLDPRT, 2051K124_CHEMICAL-RESISTANT PVC DUCT.SLDPRT, 3795K133_STAINLESS STEEL GAUGE.SLDPRT, 4596K121_THICK-WALL D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]
2020-10-27 Add STM32F4xx HAL files
2020-10-28 Add low level device files
2020-10-28 Stub inspiratory valve for testing
2020-10-28 Remove toy valve implementation
2020-10-28 Create empty valve demo task
2020-10-28 Setup pin mappings for valve control
2020-10-28 Initialize GPIO for valves
2020-10-28 Implement valve control functions
2020-10-29 Implement valve control demo task
2020-10-29 Added empty sensor file, modified units and limits in pressureFlowSensor_private.h
2020-10-30 Close valves initially in valve demo state machine
2020-10-30 Refacotr testing framework
2020-11-03 Added validation conditions for Pressure and Flow on Sensor
2020-11-03 FS6122 sensor reading pressure via i2c -> uart running in main.c
2020-11-05 Refactor sensor code and add sensor_demo task
2020-11-17 Fix pressureFlowSensor function declarations
2020-11-19 Comment sensor_demo task, add waits
2020-11-19 Rename sensor.h and sensor_private.h
2020-11-19 Disable ADC in stm324xx_hal_conf.h
2020-11-19 Remove redeclaration of result in sensor.c
2020-11-20 Write sensor values to MeasuremensStatus struct
2020-11-23 Comment serial number in sensor_private.h
2020-11-23 Handle I2C errors for sensor
2020-11-28 Implement sensor stub thanks to Alexander
2020-11-28 Update the stub to use the sensor with status
2020-11-28 fix include to sensor.h
2020-11-29 Add test chen circuit pressure too high to start inspiration
